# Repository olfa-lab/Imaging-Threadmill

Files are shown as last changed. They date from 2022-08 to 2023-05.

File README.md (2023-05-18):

## Treadmill for Imaging/Stimulation of Head Fixed Mice
  This is a treadmill for use in imaging and stimulation rigs. The design allows the animal to move and relieve stress over the course of a session while maintaining complete stability for clear signal. The treadmill is simple to assemble and was created to address concerns with weight, cost, and space. Most notably, this design accommodates the load-tolerance parameters of a goniometer, thus allowing the whole assembly to be precisely angled to achieve the most suitable field of view.

All components referenced in the assembly instructions below are listed their respective folders (.STL files for 3D printed components and specs/links for hardware).
## ASSEMBLY INSTRUCTIONS ##
### Rotation stage:
- Drill out the threads of the two middle through-holes in the metal base so that they are smooth 1/4-20 clearance holes.
- Use set screws to firmly attach metal posts on both sides of the base.
- Slide the 3D printed treadmill frame onto the base + post assembly.
- Use middle two holes in the base of the assembly to secure the base to the rotation stage/platform with 1/4-20 screws.
### Head fix clamp:
- Slide the two clamps into the channels at the top of the 3D printed frame.
- Secure directly to each mounting post with a screw and washer.
- Adjust distance by loosening the screw, sliding the clamp into position, and re-tightening the screw.
### Treadmill:
- 3D print treadmill component.
- Use tip of soldering iron to set heat-set inserts into holes in the rail guides.
- Securely attach Teflon tape along the middle track and the inside of the adjacent tracks of the treadmill.
- Place LEGO 24-tooth gears in each slot of the treadmill (4 total).
- Fasten the gears in place by threading a LEGO axle through the holes in the treadmill and the gears.
- Assemble LEGO treads, lay two strips (one over each row of gears) and snap them together.
- Lower treadmill onto the assembly (shorter end forward) and secure at desired height using a screw and washer through the slider hole/heat set insert.   
### DiamondPost (Headbar)
- diamond_post_standard_MK2 is mainly used for imaging setup. It has been designed for Nikon 16/0.8 and 10X/0.5 while using water as an immersion medium. 
- The depth of well can be smaller if you want to use less viscous medium (such as ultrasound gel).

### Versions
Mihaly Voroslakos did some modifications and his version can be found
https://github.com/misiVoroslakos/3D_printed_designs/tree/main/Treadmill_Rinberg

### Parts
Part list can be reached here. 
https://github.com/misiVoroslakos/3D_printed_designs/blob/main/Treadmill_Rinberg/BOM_Treadmill_Rinberg.txt

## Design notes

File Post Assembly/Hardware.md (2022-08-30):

The above STL file is not meant to be 3D printed. It is a reference for the post assembly onto which the treadmill and treadmill frame are mounted.

The assembly consists of the following hardware:
- (2X) RS2 - Ø1" Pillar Post, 1/4"-20 Taps, L = 2" : https://www.thorlabs.com/thorproduct.cfm?partnumber=RS2

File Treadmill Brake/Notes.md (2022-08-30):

This is a component that can be fitted onto one of the LEGO Technic axles and matched to its corresponding hole on the treadmill (middle hole from side view). In doing so you prevent the axles from rotating and therefore brake/halt all movement of the treadmill whenever necessary.

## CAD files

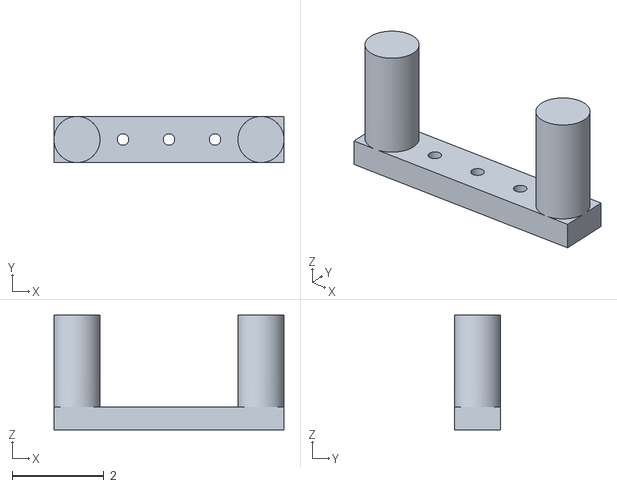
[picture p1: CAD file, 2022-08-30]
Post Assembly/Model of Mounting Assembly.stl
5.00 x 1.00 x 2.50

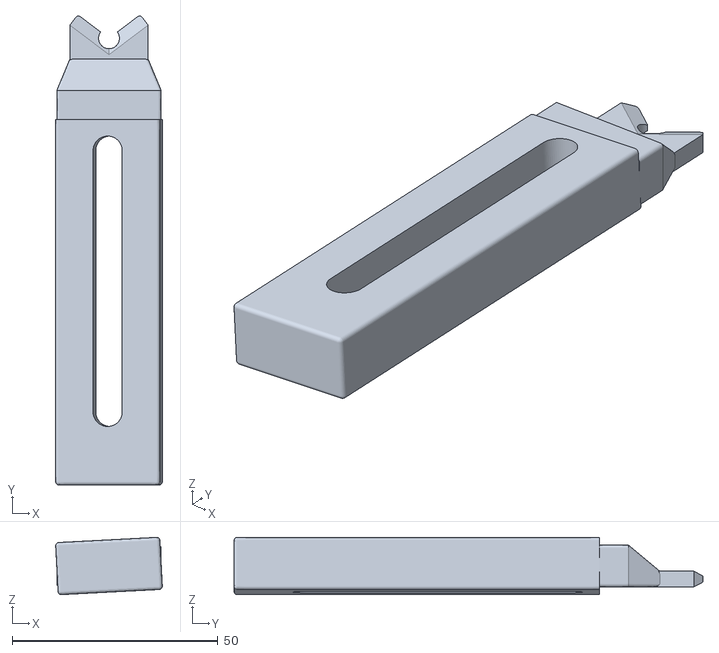
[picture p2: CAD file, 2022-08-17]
Clamps/rivetclamp_2PForWheel_3degLeft.stl
25.9 x 114.0 x 13.9

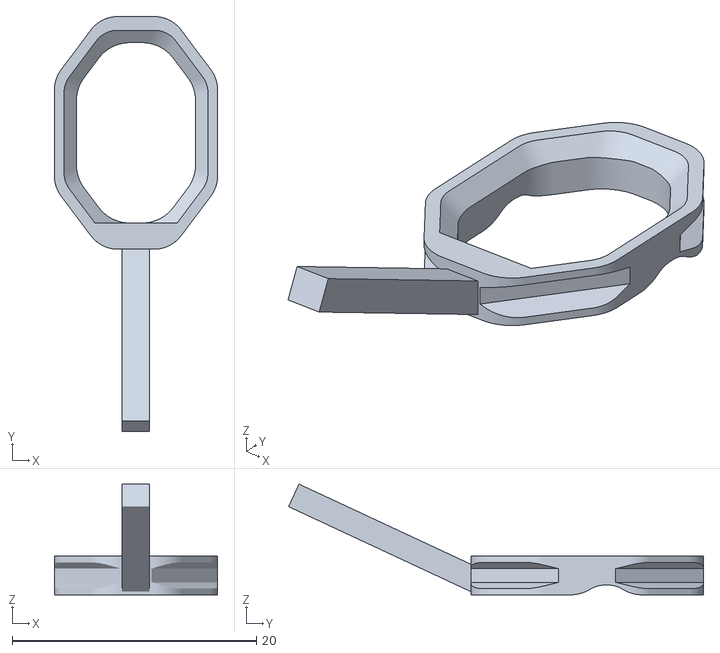
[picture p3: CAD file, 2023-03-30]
DiamondPost/diamond_big_MK.stl
13.4 x 34.0 x 9.07

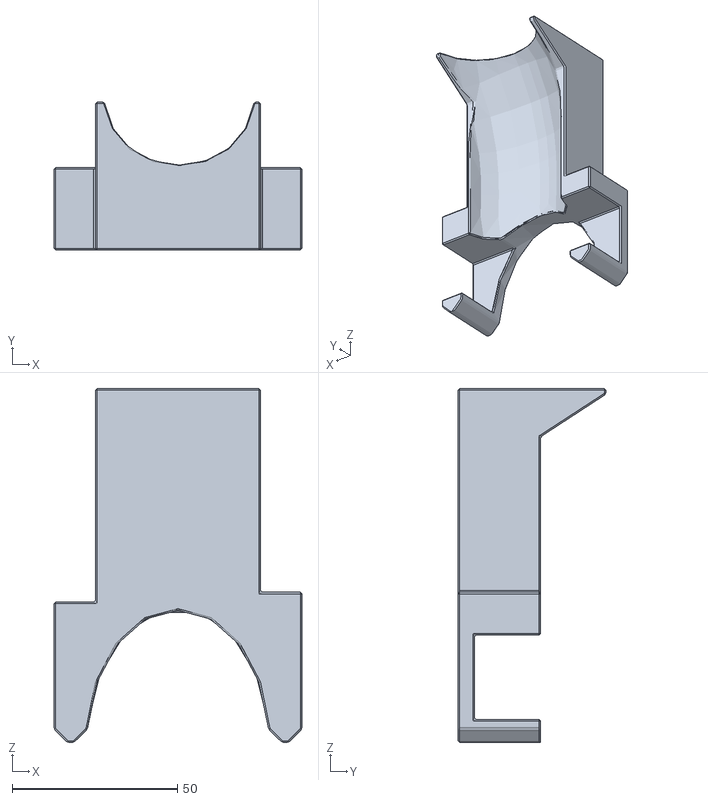
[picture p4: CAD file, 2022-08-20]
MouseCover/Mouse_Cover_Fat v1.stl
75.0 x 44.8 x 107.1

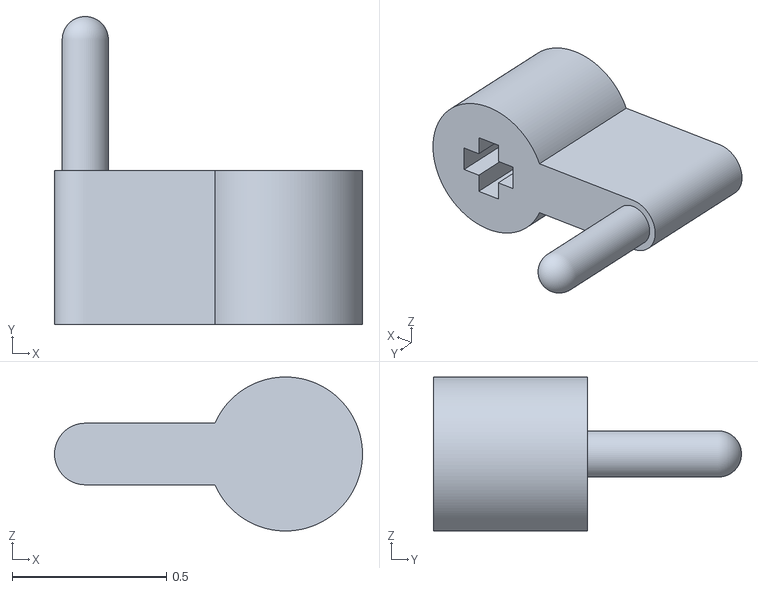
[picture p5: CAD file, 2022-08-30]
Treadmill Brake/Axle Clamp.stl
1 x 1.00 x 0.5

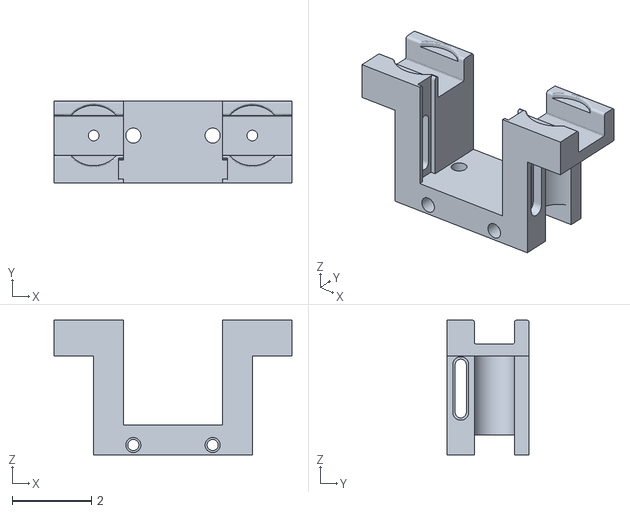
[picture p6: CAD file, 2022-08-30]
Treadmill Frame/Treadmill Frame.stl
6.00 x 2.08 x 3.40

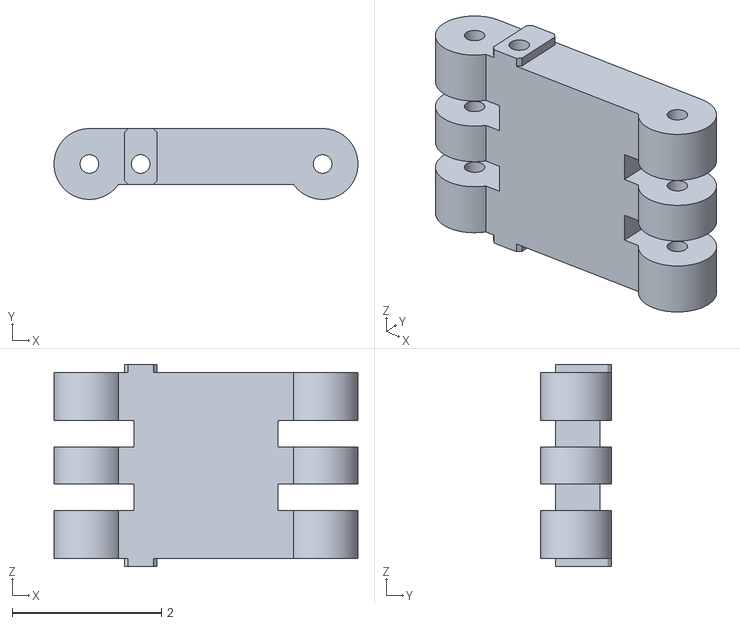
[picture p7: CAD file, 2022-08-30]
Treadmill/Treadmill.stl
4.07 x 0.95 x 2.71

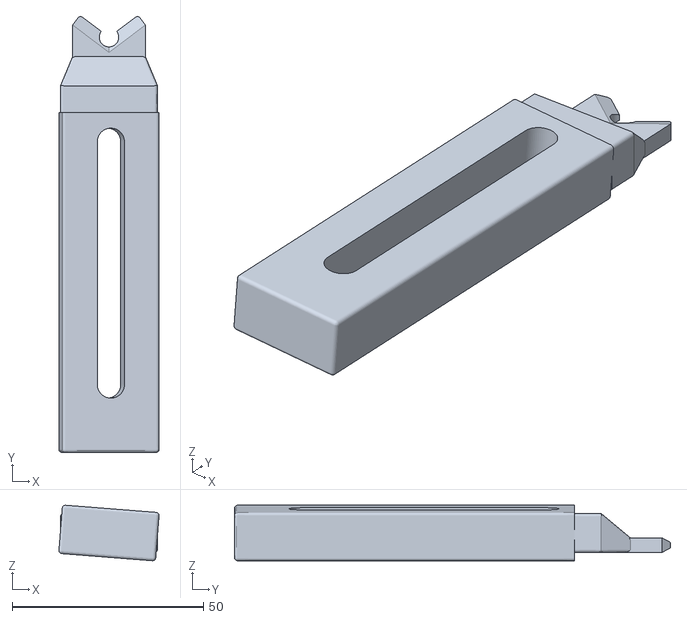
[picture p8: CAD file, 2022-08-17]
Clamps/rivetclamp_2PForWheel4p5Right.stl
26.2 x 114.0 x 14.5

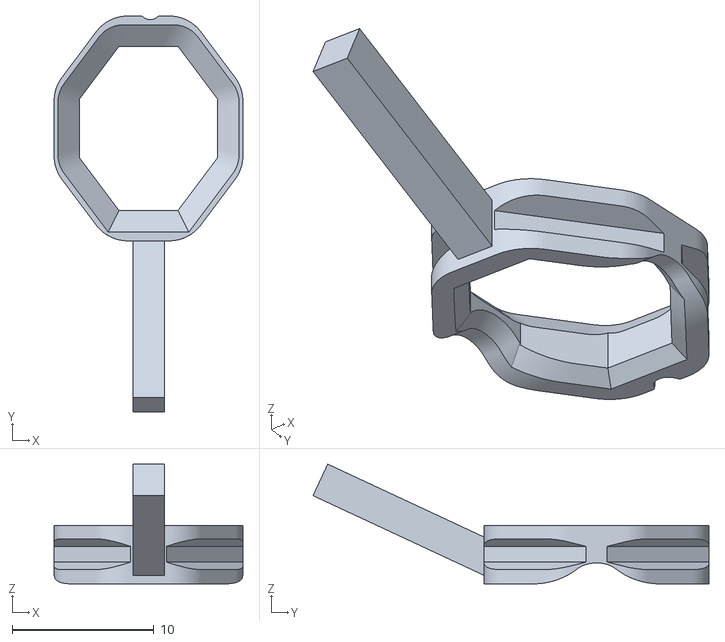
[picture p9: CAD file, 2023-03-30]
DiamondPost/diamond_post_standard_MK2.stl
13.3 x 28.0 x 8.46

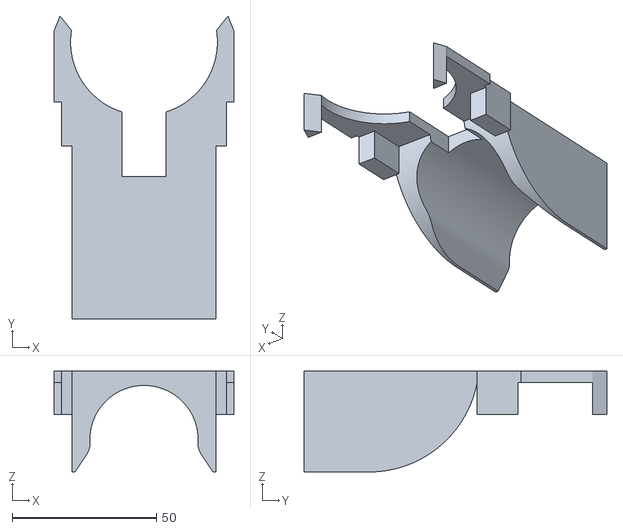
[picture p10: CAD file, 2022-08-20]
MouseCover/MouseCover_v2.stl
62.2 x 105.0 x 35.0

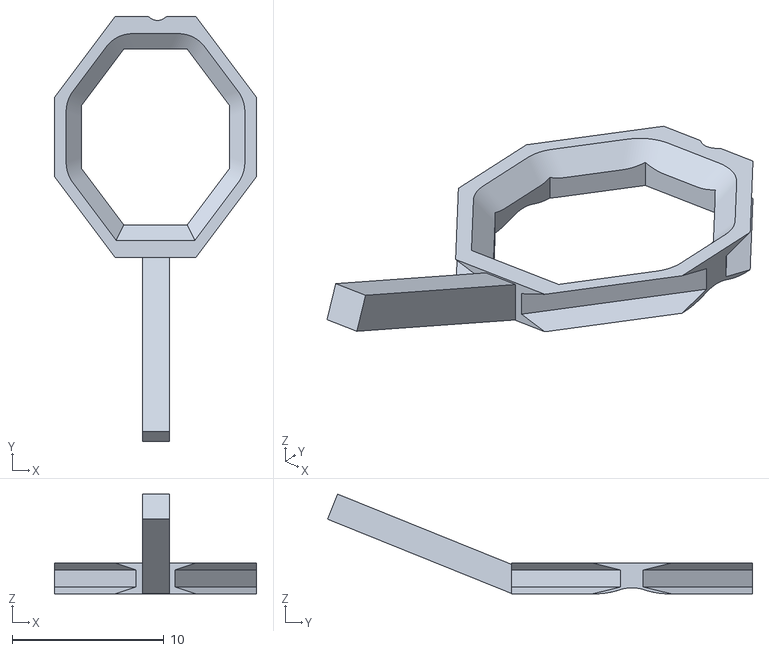
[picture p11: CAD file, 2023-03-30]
DiamondPost/diamond_post_standard_forJustin.stl
13.3 x 28.0 x 6.57

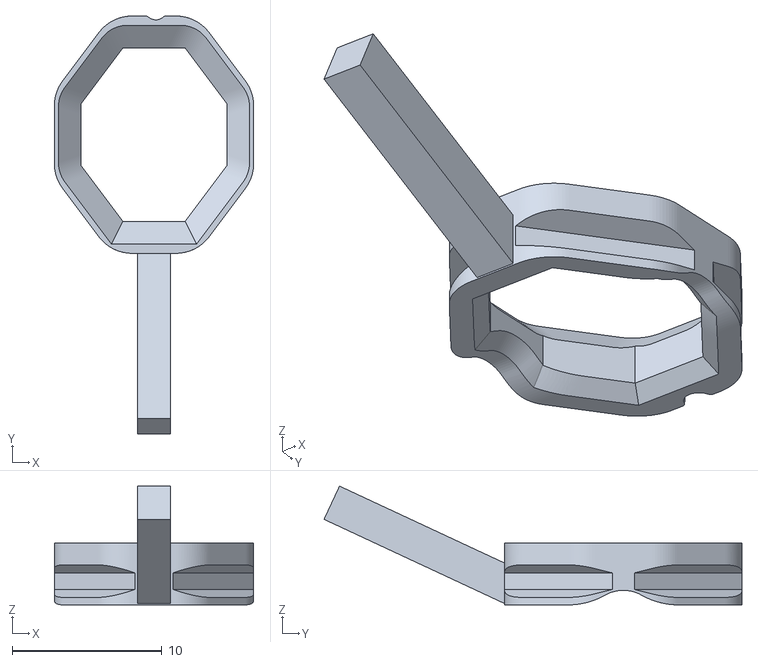
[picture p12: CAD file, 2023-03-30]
DiamondPost/diamond_post_standard_MK.stl
13.3 x 28.0 x 7.95

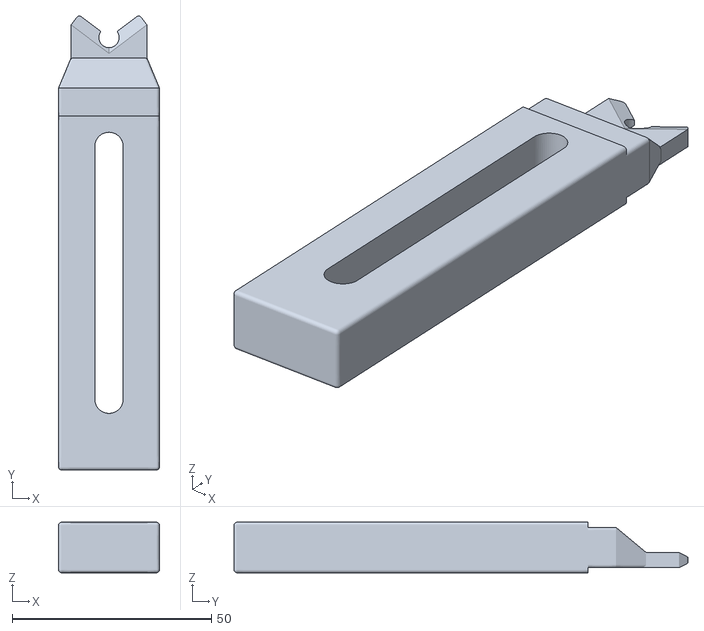
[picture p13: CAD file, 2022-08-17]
Clamps/rivetclamp_2PForWheel.stl
25.4 x 114.0 x 12.7

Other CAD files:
Clamps/rivetclamp_2PForWheel4p5Left.stl
Clamps/rivetclamp_2PForWheel_3degRight.stl
Clamps/rivetclamp_2PForWheel.ipt
DiamondPost/diamond_big_MK.ipt
DiamondPost/diamond_big_MK_V2.ipt
DiamondPost/diamond_post_standard_MK.ipt
DiamondPost/diamond_post_standard_MK2.ipt
DiamondPost/diamond_post_standard_forJustin.ipt
MouseCover/MouseCover_v2.ipt
MouseCover/Mouse_Cover_Fat v1.ipt
MouseCover/OldVersions/Part1.0005.ipt

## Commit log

2022-08-17 Clamps are added
    [rivetclamp_2PForWheel.ipt, rivetclamp_2PForWheel.stl, rivetclamp_2PForWheel4p5Left.stl, rivetclamp_2PForWheel4p5Right.stl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]
2022-08-20 Mouse Cover
    [MouseCover_v2.ipt, MouseCover_v2.stl, Mouse_Cover_Fat v1.ipt, Mouse_Cover_Fat v1.stl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]
2022-08-30 Create Treadmill Frame.stl
    [Treadmill Frame.stl]
2022-08-30 Create Post Assembly.stl
    [Post Assembly.stl]
2022-08-30 Create Axle Clamp.stl
    [Axle Clamp.stl]
